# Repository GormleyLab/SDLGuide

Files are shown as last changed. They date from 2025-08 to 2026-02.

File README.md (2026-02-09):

<p align="center">
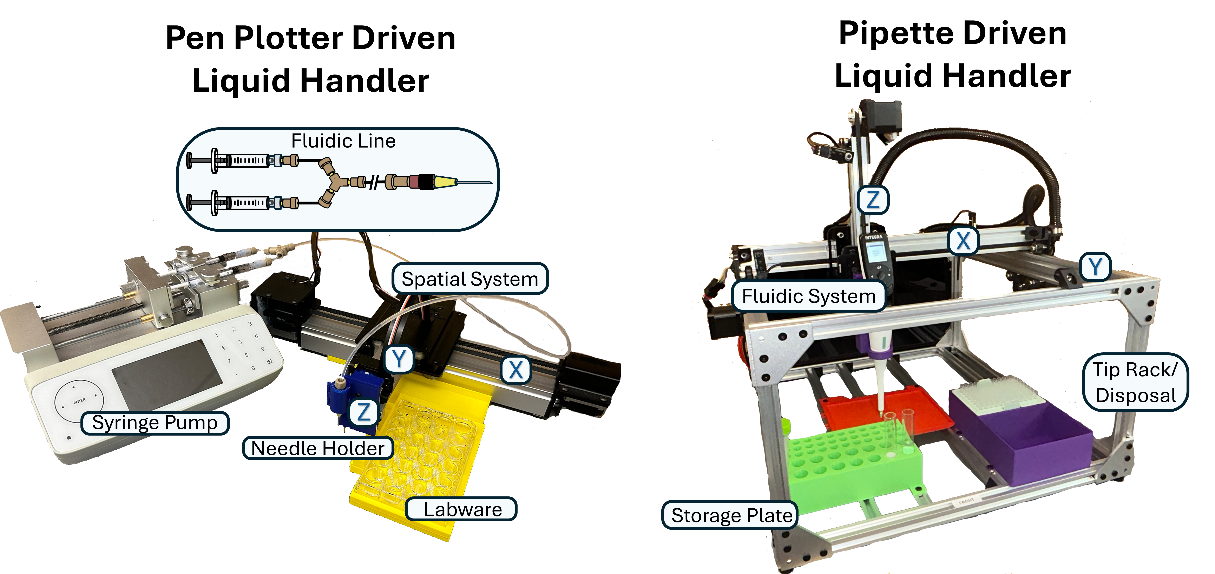
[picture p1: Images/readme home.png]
readme home
  
</p>

# Overview
Self-driving laboratories (SDLs) address a common bottleneck in experimentation: time and effort required to explore large parameter spaces. By combining automated experimentation with machine learning (ML) and Bayesian optimization (BO), an SDL can iteratively design experiments and learn from resulting data in a closed-loop, fully autonomous workflow.

This repository contains the instructions/code/files for the assembly and operations of a [Pen Plotter Driven Liquid Handler](/Pen%20Plotter%20Liquid%20Handler) and 
[Pipette Driven Liquid Handler](https://github.com/GormleyLab/Pipette-Liquid-Handler) as well as a collection of hands-on tutorial notebooks for active learning. Both devices are designed as low-cost automation tools to produce SDLs. The pen plotter-driven liquid handler is created using rigid pre-built spatial components that are modified to fit a user-developed 
fluidic system. The pipette-driven liquid handler is designed using modular components to provide the most flexibility, paired with a wireless autopipette.

In addition to hardware documentation, this repository includes a representative dataset generated using the SDL pipeline implemented here. The dataset was produced fully autonomously, and is used as an example to demonstrate how the design-build-test-learn (DBTL) workflow operates in practice, from experimental design through surrogate model training.
We use the optimization of a glucose oxidase (GOx) enzyme assay, which are common in wet-lab environments and are well suited as a representative example. 

---

## Repository Structure

Use this diagram to navigate the repository:

```
├── Hands-on Tutorial/           # AL and SDL tutorial notebooks and example data
│   ├── Notebook 1 - AL Tutorial.ipynb    # Principles of Active Learning
│   ├── Notebook 2 - SDL Tutorial.ipynb   # Real-world SDL application (enzyme assay)
│   ├── GOx Assay data_bank_renamed.csv  # Example GOx assay data for tutorials
│   ├── Older Iterations/               # Previous notebook versions
│   ├── requirements.txt                # Python dependencies for tutorials
│   └── README.md
│
├── Pen Plotter Liquid Handler/   # AxiDraw-based liquid handler (hardware + software)
│   ├── Pen Plotter SDL Software/ # GUI and automation software
│   │   ├── data/
│   │   │   └── GOx Assay data_bank.csv  # Validation dataset example
│   │   ├── src/
│   │   │   ├── sdlgui.py         # Main GUI layout and logic
│   │   │   ├── guifunctions.py   # Experiment setup, seed library, dispensing
│   │   │   ├── liquidhandler.py  # AxiDraw and syringe pump control
│   │   │   ├── dataprocessing.py # Data extraction, ML/AL integration
│   │   │   └── sdlvariables.py   # Global variables and experiment state
│   │   ├── resources/            # Icons and assets
│   │   ├── main.py               # Entry point (runs the GUI)
│   │   ├── requirements.txt
│   │   └── README.md
│   ├── SDL CAD Files/                  # 3D printable parts (STL, STEP)
│   ├── Pen Plotter LH Build Guide.pdf  # Building instructions for hardware
│   ├── SDL_SOP.pdf                     # Standard operating procedure
│   └── README.md
│
├── Pipette Liquid Handler/       # Wireless autopipette-based liquid handler (External Repo)
│   ├── Pipette SDL Software/    # GUI and automation software
│   │   ├── data/
│   │   │   └── GOx Assay data_bank.csv  # Validation dataset example
│   │   ├── src/
│   │   │   ├── sdlgui.py         # Main GUI layout and logic
│   │   │   ├── guifunctions.py   # Experiment setup, seed library, dispensing
│   │   │   ├── liquidhandler.py  # Pipette and pump control
│   │   │   ├── dataprocessing.py # Data extraction, ML/AL integration
│   │   │   └── sdlvariables.py   # Global variables and experiment state
│   │   ├── resources/            # Icons, tip positions, RemoteControl
│   │   ├── main.py               # Entry point (runs the GUI)
│   │   ├── requirements.txt
│   │   └── README.md
│   ├── Config Files/            # G-code and controller config (config.g, homeall.g, etc.)
│   ├── Pipette CAD Files/       # 3D design files (needle holder, vial rack, etc.)
│   ├── WIP Controller Program/   # Work-in-progress controller script alternatives
│   ├── Pipette Liquid Handler Building Guide.pdf
│   ├── Pipette Liquid Handler Parts List.xlsx
│   └── README.md
│
├── Images/                      # Figures for README and docs
├── index.html                    # Project homepage
├── LICENSE
└── README.md                     # This file
```

**Quick links:** [Tutorial Notebook 1 (AL)](/Hands-on%20Tutorial/Notebook%201%20-%20AL%20Tutorial.ipynb) · [Tutorial Notebook 2 (SDL)](/Hands-on%20Tutorial/Notebook%202%20-%20SDL%20Tutorial.ipynb) · [Pen Plotter Liquid Handler](/Pen%20Plotter%20Liquid%20Handler) · [Pipette Liquid Handler](https://github.com/GormleyLab/Pipette-Liquid-Handler)

---

## Tutorial Overview
The goal of the provided tutorial is to walk through the essentials of AL from start to finish, providing both conceptual explanations and hands-on code examples. A basic understanding of ML is assumed. If you're new to ML, we highly recommend reviewing [Part 1 of our User’s Guide series](https://doi.org/10.1021/acspolymersau.2c00037).
This guide is structured into three main tutorial notebooks, each building on the last for a smooth learning experience. Major points of interest from the guide provided are discussed below. 
### [Tutorial Notebook 1: Principles of Active Learning ](/Hands-on%20Tutorial/Notebook%201%20-%20AL%20Tutorial.ipynb)  
We begin with a simple, two-dimensional example of **Bayesian Optimization (BO)** applied to a black-box function. This notebook introduces the foundational concepts of active learning, inccluding data seeding, fitting surrogate models to data, and applying various acquisition functions to choose new sampling points.

### [Tutorial Notebook 2: Application to Real-World Data - Self-Driving Labs](/Hands-on%20Tutorial/Notebook%202%20-%20SDL%20Tutorial.ipynb)
Finally, we apply AL to a real experimental dataset involving enzymes. This notebook demonstrates how active learning can be used to efficiently select informative experiments and accelerate discovery in scientific research. This notebook explores: seed library generation (initial sampling) and closing the loop in the context of an SDL.

---

## Abstract
Experimentation is inherently difficult because most methods require substantial refinement, calibration, and validation before high-quality, reliable data can be collected. In most cases, experimental domains have multiple variables (i.e., high dimensionality), thus requiring their simultaneous optimization for single and multi-objective targets. Traditional experimental approaches rely on trial-and-error methods guided by rational decision making, but these become increasingly inefficient and ineffective as complex interactions between inputs limit our ability to capture underlying trends using conventional statistical approaches. Active learning and machine learning (AL/ML) combined with automation represents an indispensable approach for future laboratory productivity. However, a steep initial learning curve and high costs of instrumentation pose substantial barriers to adopt this powerful approach. To democratize access, we provide a comprehensive tutorial covering both the computational skills and hardware implementation necessary for self-driven experimental workflows. The accompanying open-source, low-cost liquid handling platforms offer practical templates for researchers adopting self-driving lab (SDL) methodologies.

---

## Authors:
Apostolos Maroulis, Dylan Waynor<br>
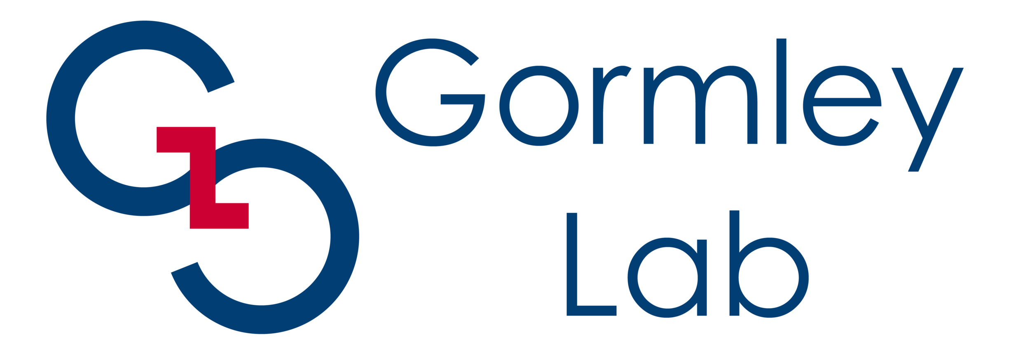
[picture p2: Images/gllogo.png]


Last Updated 01/29/2026
Version 1.0.0

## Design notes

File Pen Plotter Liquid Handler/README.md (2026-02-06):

# Self-Driving Lab based on AxiDraw and Syringe Pump
<p align="center">
axidraw
</p>

This project provides a graphical user interface (GUI) for automating enzyme assay experiments using a custom-built AxiDraw pen plotter liquid handler and a SpectraMax M2plate reader. It enables users to design, dispense, and analyze experimental formulations with minimal manual intervention.

## Features

- GUI for experiment setup and control
- Automated liquid handling via AxiDraw
- Integration with SpectraMax plate reader
- Seed library generation using Latin Hypercube Sampling
- Automated data collection and analysis
- Machine learning-driven experiment optimization (Gaussian Process, Expected Improvement)
- Custom CSV import/export for formulations and results

## Directory Structure

```
├── data/
│   └── GOx Assay data_bank.csv  # Validation dataset example
├── src/
│   ├── sdlgui.py         # Main GUI layout and logic
│   ├── guifunctions.py   # Experiment setup, seed library, dispensing
│   ├── liquidhandler.py  # AxiDraw and syringe pump control
│   ├── dataprocessing.py # Data extraction, ML/AL integration
│   └── sdlvariables.py   # Global variables and experiment state
├── resources/            # Icons and assets
├── main.py               # Entry point (runs the GUI)
├── requirements.txt
└── README.md
```

## Getting Started

### Prerequisites

- Python 3.8+
- [requirements.txt](requirements.txt) dependencies
- AxiDraw hardware and drivers
- SpectraMax plate reader and SDK
- ChemyX Syringe Pump SDK

### Installation

```sh
git clone <https://github.com/GormleyLab/SDLGuide>
cd Pen Plotter Liquid Handler/Pen Plotter SDL Software
pip install -r requirements.txt
```

### Running the Program

```sh
python main.py
```

## Usage

- **Home Tab:** Input reagent names, concentrations, pH, and group assignments. Import custom CSVs if needed.
- **Enzyme Assay Tab:** Configure experiment parameters, bounds, and desired activity. Start automated DBTL (Design-Build-Test-Learn) cycles.
- **Liquid Handler Tab:** Manually control AxiDraw for dispensing. (WIP)
- **Manual Tab:** Directly move AxiDraw and adjust pen/syringe settings.

---

### [Standard Operating Procedure (SOP)](SDL_SOP.pdf)

#### Self-Driven Lab: Custom Liquid Handler SOP

This SOP provides relevant information necessary for the overall viability and use of our device. It is reliant on basic understanding of other supplemental information: References to device setup will be attributed to the system build guide. References to ML/AL will be attributed to the tutorial notebooks. Some constraints of the device are in place to balance price effectiveness and system performance to provide a low-cost example of a liquid handler. The following is a quick start guide. It is highly recommended to follow the linked SOP above for an in-depth guide.

---

#### 1. Hardware Setup

To adapt the AxiDraw Pen Plotting machine for liquid handling, several modifications are required.  
Refer to the [Pen Plotter LH Build Guide](/Pen%20Plotter%20Liquid%20Handler/Pen%20Plotter%20LH%20Build%20Guide.pdf) for a detailed walkthrough of the necessary mechanical and hardware changes.  

1. **3D print the following custom parts**:  
   - AxiDraw Needle Holder  
   - AxiDraw Well Plate Platform  
   - Large Reservoir Insert  
2. **Modify** the AxiDraw hardware as outlined in the guide.  
3. **Assemble the fluidic loop** and connect it to both the Chemyx syringe pump and the AxiDraw.  
---

#### 2. Software Setup

- **AxiDraw:**  
  [AxiDraw Python API](https://axidraw.com/doc/py_api/#introduction)  
  If you haven't already, install:  
  `python -m pip install https://cdn.evilmadscientist.com/dl/ad/public/AxiDraw_API.zip`
- **Chemyx Syringe Pump:**  
  [Chemyx Python Setup Guide](https://chemyx.com/resources/knowledge-base/general-syringe-pump-info/computer-control-programs/python-program-installation-set-up-for-chemyx-fusion-200x-syringe-pump/)

---

#### 3. Preparation For Experimentation

**3.1 Calibration Protocol:**  
- Syringe Pump Calibration: Dispense triplicate known volumes, measure mass, and calibrate for loss.
- X/Y calibration: Use Manual UI to ensure coordinates for wells, waste, and reagents are accurate.
---

**3.2 Initial Setup**

- Fill the loop with water, minimizing air bubbles.
- Align the device with the Spectramax M2 by first raising the device to the appropriate height, and then ensuring the drawer opening just clears the cutout in the AxiDraw platform.
- Fill reservoirs 1 and 3 with DI water, leaving reservoir 2 (the middle) empty for waste.

---

**3.3 Experimental Setup**

- **Experiment Configuration:**
    - Prepare reagent list with concentrations and pHs.
    - Set mixing order and concentration bounds.
    - Define desired activity (ΔOD).
    - Ensure total dispensing volume per reagent is under 1.6ml.
    - Group reagents as needed; buffers can have different types and pHs.

---

**4.3 Notes on Experimentation**

- **Reagent Order:**  
  Dispense substrate last to control reaction start.
- **Locations:**  
  Log positions for reagents, waste, storage, and cleaning troughs in the script, as well as the pen down position to be at or near the bottom of each well without putting pressure.
- **Compatibility:**  
  Check tubing and luer compatibility for solvents and biologics. Adjust calibration for viscous materials.
- **Cleaning Protocol:**  
  Flush system after use, replace disposable components, and reprime as needed.

---

Thank you for trying to use our device as a platform for a SDL.

---

## Main Modules

- [`src/sdlgui.py`](src/sdlgui.py): Main GUI logic and layout
- [`src/guifunctions.py`](src/guifunctions.py): Experiment setup, seed library generation, dispensing instructions
- [`src/liquidhandler.py`](src/liquidhandler.py): AxiDraw and ChemyX pump control
- [`src/dataprocessing.py`](src/dataprocessing.py): Data extraction, analysis, machine learning
- [`src/sdlvariables.py`](src/sdlvariables.py): Global variables and experiment state

## License

MIT License

## Authors:
Apostolos Maroulis, Dylan Waynor<br>


Last Updated 01/29/2026
Version 1.0.0

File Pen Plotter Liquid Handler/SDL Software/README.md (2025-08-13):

# Self-Driving Lab based on AxiDraw and Syringe Pump
<p align="center">
axidraw
</p>

This project provides a graphical user interface (GUI) for automating enzyme assay experiments using a custom-built AxiDraw pen plotter liquid handler and a SpectraMax M2plate reader. It enables users to design, dispense, and analyze experimental formulations with minimal manual intervention.

## Features

- GUI for experiment setup and control
- Automated liquid handling via AxiDraw
- Integration with SpectraMax plate reader
- Seed library generation using Latin Hypercube Sampling
- Automated data collection and analysis
- Machine learning-driven experiment optimization (Gaussian Process, Expected Improvement)
- Custom CSV import/export for formulations and results

## Directory Structure

```
main.py
README.md
requirements.txt
data/
    GOx Assay data_bank.csv
resources/
    gl_logo.ico
src/
    dataprocessing.py
    guifunctions.py
    liquidhandler.py
    sdlgui.py
    sdlvariables.py
```

## Getting Started

### Prerequisites

- Python 3.8+
- [requirements.txt](requirements.txt) dependencies
- AxiDraw hardware and drivers
- SpectraMax plate reader and SDK
- ChemyX Syringe Pump SDK

### Installation

```sh
git clone <repo-url>
cd SDL_6_3_25
pip install -r requirements.txt
```

### Running the Program

```sh
python main.py
```

## Usage

- **Home Tab:** Input reagent names, concentrations, pH, and group assignments. Import custom CSVs if needed.
- **Enzyme Assay Tab:** Configure experiment parameters, bounds, and desired activity. Start automated DBTL (Design-Build-Test-Learn) cycles.
- **Liquid Handler Tab:** Manually control AxiDraw for dispensing. (WIP)
- **Manual Tab:** Directly move AxiDraw and adjust pen/syringe settings.

---

### [Standard Operating Procedure (SOP)](SDL_SOP.pdf)

#### Self-Driven Lab: Custom Liquid Handler SOP

This SOP provides relevant information necessary for the overall viability and use of our device. It is reliant on basic understanding of other supplemental information: References to device setup will be attributed to the system build guide. References to ML/AL will be attributed to the tutorial notebooks. Some constraints of the device are in place to balance price effectiveness and system performance to provide a low-cost example of a liquid handler. The following is a quick start guide. It is highly recommended to follow the linked SOP above for an in-depth guide.

---

#### 1. Hardware Setup

To adapt the AxiDraw Pen Plotting machine for liquid handling, several modifications are required.  
Refer to the [Pen Plotter LH Build Guide](https://github.com/Pasta1107/Users-Guide-to-SDL/blob/main/Pen%20Plotter%20Liquid%20Handler/Pen%20Plotter%20LH%20Build%20Guide.pdf) for a detailed walkthrough of the necessary mechanical and hardware changes.  

1. **3D print the following custom parts**:  
   - AxiDraw Needle Holder  
   - AxiDraw Well Plate Platform  
   - Large Reservoir Insert  
2. **Modify** the AxiDraw hardware as outlined in the guide.  
3. **Assemble the fluidic loop** and connect it to both the Chemyx syringe pump and the AxiDraw.  
---

#### 2. Software Setup

- **AxiDraw:**  
  [AxiDraw Python API](https://axidraw.com/doc/py_api/#introduction)  
  If you haven't already, install:  
  `python -m pip install https://cdn.evilmadscientist.com/dl/ad/public/AxiDraw_API.zip`
- **Chemyx Syringe Pump:**  
  [Chemyx Python Setup Guide](https://chemyx.com/resources/knowledge-base/general-syringe-pump-info/computer-control-programs/python-program-installation-set-up-for-chemyx-fusion-200x-syringe-pump/)

---

#### 3. Preparation For Experimentation

**3.1 Calibration Protocol:**  
- Syringe Pump Calibration: Dispense triplicate known volumes, measure mass, and calibrate for loss.
- X/Y calibration: Use Manual UI to ensure coordinates for wells, waste, and reagents are accurate.
---

**3.2 Initial Setup**

- Fill the loop with water, minimizing air bubbles.
- Align the device with the Spectramax M2 by first raising the device to the appropriate height, and then ensuring the drawer opening just clears the cutout in the AxiDraw platform.
- Fill reservoirs 1 and 3 with DI water, leaving reservoir 2 (the middle) empty for waste.

---

**3.3 Experimental Setup**

- **Experiment Configuration:**
    - Prepare reagent list with concentrations and pHs.
    - Set mixing order and concentration bounds.
    - Define desired activity (ΔOD).
    - Ensure total dispensing volume per reagent is under 1.6ml.
    - Group reagents as needed; buffers can have different types and pHs.

---

**4.3 Notes on Experimentation**

- **Reagent Order:**  
  Dispense substrate last to control reaction start.
- **Locations:**  
  Log positions for reagents, waste, storage, and cleaning troughs in the script, as well as the pen down position to be at or near the bottom of each well without putting pressure.
- **Compatibility:**  
  Check tubing and luer compatibility for solvents and biologics. Adjust calibration for viscous materials.
- **Cleaning Protocol:**  
  Flush system after use, replace disposable components, and reprime as needed.

---

Thank you for trying to use our device as a platform for a SDL.

---

## Main Modules

- [`src/sdlgui.py`](src/sdlgui.py): Main GUI logic and layout
- [`src/guifunctions.py`](src/guifunctions.py): Experiment setup, seed library generation, dispensing instructions
- [`src/liquidhandler.py`](src/liquidhandler.py): AxiDraw and ChemyX pump control
- [`src/dataprocessing.py`](src/dataprocessing.py): Data extraction, analysis, machine learning
- [`src/sdlvariables.py`](src/sdlvariables.py): Global variables and experiment state

## License

MIT License

## Authors:
Apostolos Maroulis, Dylan Waynor<br>


Last Updated ***

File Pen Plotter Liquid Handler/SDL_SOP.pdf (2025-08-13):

# Self-Driven Lab: Custom Liquid Handler SOP

By: Apostolos Maroulis, Dylan Waynor

This SOP provides relevant information necessary for the overall viability and use of our device. However, it is reliant on basic understanding of other supplemental information: References to device setup will be attributed to the system build guide. References to ML/AL will be attributed to the Google Colab notebook. Some constraints of the device are in place to balance price ef ectiveness and system performance to provide a low cost example of a liquid handler.

# Section 1. Hardware Setup

If a user creates a custom liquid handler based on the provided guide we would like to provide a small explanation of our example setup connected to a UV spectrophotometer. One of the major limitations of the device is its clearance when interacting with other devices to remedy this we used pipette tip holding boxes to elevate the device to the proper height. Any solid/stable object will work.

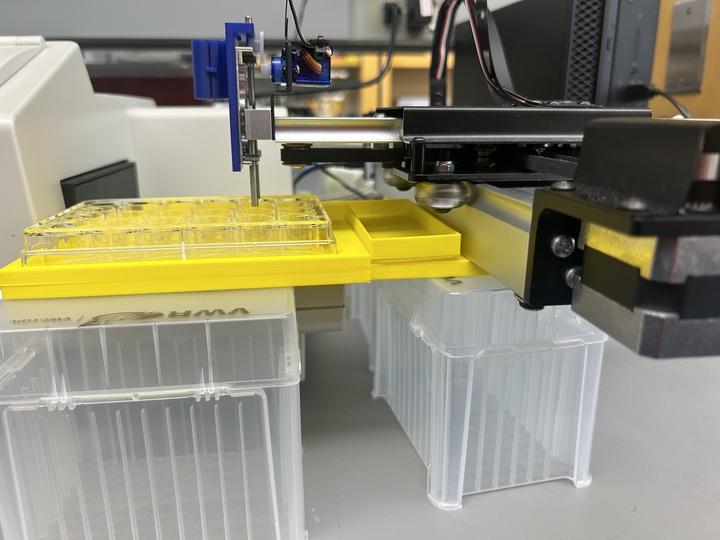
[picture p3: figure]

We align the device to the open tray of the UV spectrophotometer. The consistent measurement of this orientation is important as the positions of the measurement plate wells depend on your choice of positional values. (the positions attributed to the reagent wells and storage troughs should be always consistent as they are connected to the device).

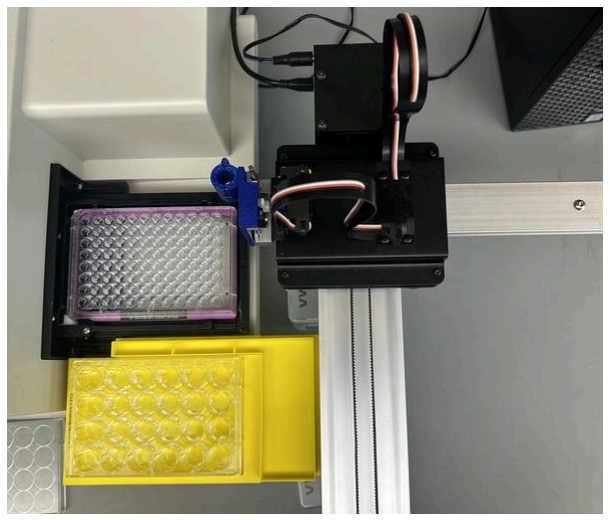
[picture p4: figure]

# Section 2. Software setup

To use the devices in the provided (or your own) python scripts it is important to download the relevant packages for the corresponding commands.
Axidraw - https://axidraw.com/doc/py_api/#introduction
One line install - python -m pip install https://cdn.evilmadscientist.com/dl/ad/public/AxiDraw_API.zip

Chemyx Syringe Pump -
https://chemyx.com/resources/knowledge-base/general-syringe-pump-info/computer-control-programs/python-program-installation-set-up-for-chemyx-fusion-200x-syringe-pump/ (https://chemyx.com/resources/knowledge-base/general-syringe-pump-info/computer-control-programs/python-program-installation-set-up-for-chemyx-fusion-200x-syri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)

# Section 3. Preparation For Experimentation

### 3.1. Calibration of Fluidic System

As you finish the construction of the fluidic system of the liquid handler there are additional setup steps before the device is truly experimentally ready.

### 3.1.1 Explanation of syringe choice and design

The complete design setup utilizes a two-syringe system that seeks to minimize variability of the syringe pump. Two 1ml syringes were chosen to leverage a smaller internal diameter to increase the reliability of dispense liquid at the flow rates used [Cite - Melanie A Jordan paper]. A longer syringe used within the system gives more available stroke length to leverage for better control of the stepper motor that controls the syringe pump. The discrete stopping positions of the syringe pump only allow for a specific volume of fluid to flow, and by having more discrete points it is possible to generate a greater number of specific volumes. The complete design setup utilizes a two-syringe system that seeks to minimize variability of the syringe pump. This is done by having longer syringes with small diameters. However, by optimizing for the most accuracy total volume does suffer. Larger syringes can be retrofitted into the design for an increase in possible sample volume for the cost of dispensing accuracy.

### 3.1.2 Storage Loop Setup

The fluidic system is based on a pressure driven syringe pump. To have the ability to draw and dispense small volumes using this system, we use a storage loop. This loop is filled with an incompressible experimentally inert fluid such as water to create consistent pressure using Pascal's principle. For this principle to be as true as possible, the minimization of air (bubbles) that is introduced into the storage solution is very important. To achieve as little air introduced into the syringes and loop the initial filling process should be done carefully.
To initially fill the syringes we fill a large vessel with the storage fluid (water) and fully submerge and evacuate the air that is trapped within. Then using the luer connectors reattach the partially filled tubes, and evacuate any remaining air out of the tubes (this is generally done by flicking the side of the tubes to jostle the settled air bubbles.
To generally reduce the reintroduction of air bubbles in the system we were able to improve performance by the leveling of your storage loop tubing to reduce air lock formation and waterfall flow at local maximas in height.
Another possible introduction of air within your syringes itself is dependent on the syringe choice. Lower quality syringes may not have plunger tips with perfect seals when drawing or dispensing at high rates. Due to this phenomena sometimes occurring the reduction in overall flow rates may help to improve inaccuracies as a tradeoff to total experimental time.

### 3.1.3 Air Gap

To separate the storage loop fluid from your drawn reagents we utilize a small air gap. This idea is not perfectly ideal as it introduces pressure loss when interacting with a compressible gas. However, compared to alternative methods like using an immiscible fluid as the representative gap, issues of mixing are greatly lessened. When the’ drawing protocol’ is executed during experimentation this air gap is formed as the buffer and should keep as a single unit if general bubble prevention protocol is followed. If it is noticed that there is a particular breakup of the air gap it may be produced by alterations in the surface energy of the tubing. To reduce this general cleaning protocol may be necessary.

# Section 4 Experimental Protocol

### Section 4.1 Manual Tab

Provided with the experimental UI, we created a mechanism to independently control the spatial system for the purposes of manual setup (Due to the easy to use interface on the Chemyx syringe pump the manual UI does not have controls for the pump). The manual setup stage of the system is very important for preallocating global variables before any automation steps are tried.

### 4.1.1 Variable Setup

- speed_pendown, speed_penup

These values designate the added degree of speed of the needle tip moving up and down at a location (range 0-110)Values can be changed if one would like to optimize the total time of experimentation. (The notation of variables using ‘pen’ is based on the fact that the axidraw system usually uses its z axis to move a pen up and down for writing tasks)

- pen up/down position and limit

These values contain the desired "top" and "bottom" positions of the z axis (range 0-100). A top position at 100 signifies that we would like to have the initial position at maximum height. The bottom positions may be altered to dispense into a vessel without hitting its bottom (in our case the bottom of a single well). A known issue is droplet formation occurring and adhering at the needle tip. It may be relevant to obtain precise measurements of the dispensing/ drawing position to allow for the reduction of droplet formation interfering with the accuracy of the device. To find optimal positioning there will be some trial and error.

- Positional calibrations (X/Y positions)

Using the Manual UI you are able to alter the X/Y spatial position of the axidraw system. This capability is introduced to allow the user to identify the specific coordinates that correlate with their experimentation. This feature is used to locate the position of the first well, waste, reagent holders. However this gained knowledge must be transferred into the relevant points within the script.

### 1.3 Calibration Protocol

To conclude general setup we suggest using a calibration step to understand how well you have done with setting up the fluid system and identify the loss that is generated through interactions of fluid mechanics. Some additional loss factors that are intrinsic to the system such as interactions with the tubing itself can not be helped. Therefore, it is necessary to retroactively correct the volumes used for experimentation for the loss that is consistent in your system.
To do this we use the relationship between mass and volume with a fluid of known density. We execute a sweep of volumes across the probable dispensing range (5-200ul) (Manually controlled through the Chemyx UI). In between each volume dispensed we measure the change in mass using a zeroed scale. This is recorded in triplicates to obtain readings that compare the desired dispensing volume and the measured volume. Using this data we can identify any loss trends and calibrate the system to correct for the error. Finally using the new calibration factor we identify the new accuracy using the same method. Alternative methods that can be used to identify the accuracy at specific volumes may include slowly drawing the dispensed volumes using a pipette. However, this method may be slower and more susceptible to human error.

### Section 4.2 Experimental tab

### 4.2.1 How to configure an experiment

You will need to design your parameter space, so you will need:
1. Reagent list with concentrations (and pHs if necessary)
2. Mixing Order
3. Reagent Concentration bounds (Final concentration in the well)
4. Desired activity (vMax)

5. The initial number of samples (Calculate the total volume of dispensing for each reagent and have it be under 1.6ml, including “filler”)
Capabilities of the program:
Can group reagents together, where each group gets a specific molarity based on the bounds of the reagents in the group. Then one of the reagents in the group will be selected. You can control what percentage of the seed library will contain reagents from a group. # Half of the seed library will contain reagents from a group.

Furthermore, you can add buffers, with different pHs. You can also have different buffer types, and then the program will select a buffer molarity, buffer type, and then a pH for each composition.

### 4.2.2 User Interface (UI) Info Guide

Once a wanted experimental pipeline has been thought up, one must use the UI to translate it into an automated loop.
1) You should first name the reagents in order of which they show up in your reagent reservoirs. The filler is not included in this bar, it is implied that the first reservoir is your filler material.
2) You must then identify if any reagent identifies. [i.e if you are using 3 different pH of the same buffer solution they would be in the same buffer 1 group]
3) Then you must input all reagent concentrations, each reagent concentration is non dimensionalized with respect to volume. [i.e. ABTS 200 is a 1X solution of 0.00173 mg/uL, while ABTS 100 represents a 0.5X solution] The order of concentration values determine the placement of your reagent reservoirs.
4) If a pH value is required [buffer group] you mark this reagent and leave all other reagents blank.

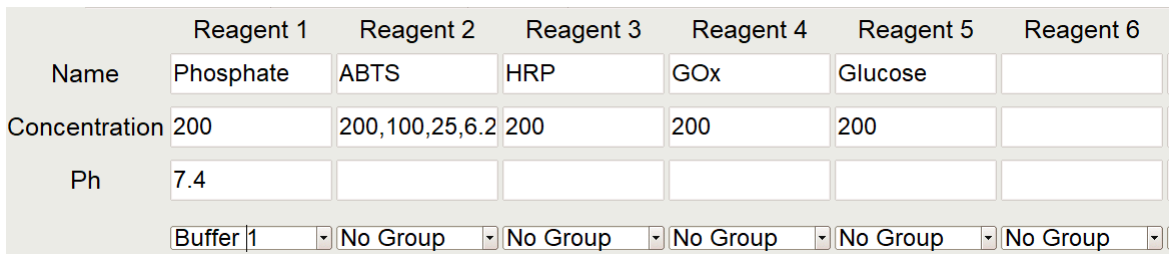
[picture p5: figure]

Non dimensionalized to volume : equivalent to the concentration value.

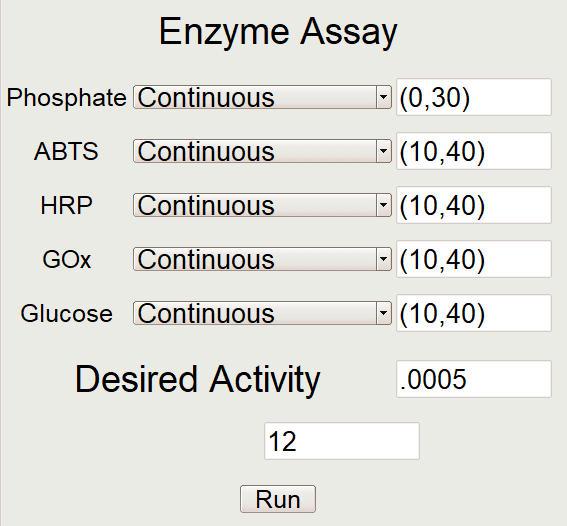
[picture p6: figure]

### 4.3. Notes on Experimentation

This section will identify helpful information for the development of your experimental procedures.

### 4.3.1 Choosing Reagent Order

A small note when setting up your design space and it is translated into the data sheet that runs the experiments. It is important to understand the ordering that the device will draw and dispense a specific reagent to formulate your mixtures. In our case, an enzymatic process does not begin its reaction until a specific substrate has been introduced. This required the ordering of the dispensed reagents to be tailored so that the reaction does not begin before we are ready to analyze the mixtures. The order may also need taking into account when thinking about possible mixing that could occur using the low cost system. Within the storage loop residue is reduced as much as it can with a cleaning stage, but the tubing may still have interactions with subsequent reagents. It may be necessary to order the reagents in order for reduction of fouling your experiment.

### 4.3.2 Reagent, Waste, Storage Solution, and Cleaning Troughs

For each component of your experiment the specific locations must be identified and logged into the script for use within the dispensing/drawing procedure. An issue that is apparent with the limited z axis depth is that to have additional objects within the range of the axidraw’s capabilities it must not interfere with X/Y movement. This produces a strict height requirement. To work within this constraint we utilized a 24-well well plate to hold our reagents, this is to hold a larger amount of volume of individual reagents that can be used uninterrupted over each iteration.. Our waste, storage, and cleaning troughs are all held in in-house creations of 3D printed troughs to be within these parameters. As an added complication to integrate with an analysis device it may be necessary to raise the entire device using stable structures to be able to correctly interface.

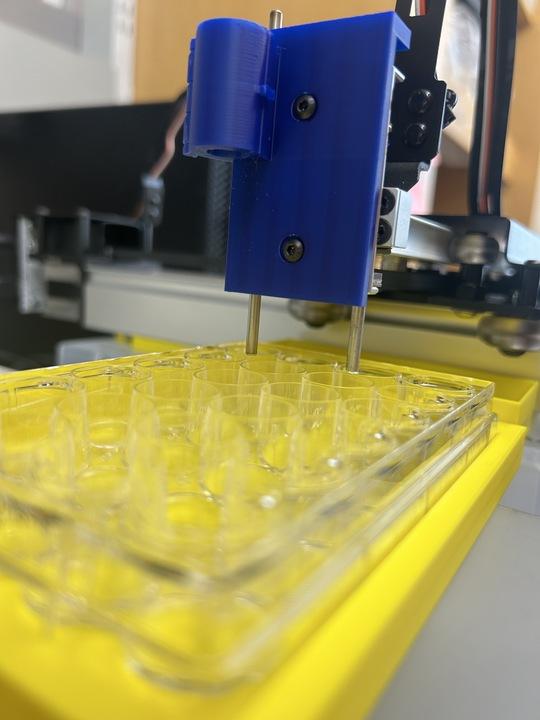
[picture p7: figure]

### 4.3.3 Compatibility (biologics, solvents, highly viscous materials)

Compatibility with solvents will be designated by tubing and luer products reference sheets. Compatibility with biological and viscous media may interfere with the fluid mechanics that drive our pressure driven system, however alterations in design or calibration may remedy these issues.

### 4.3.4 Cleaning Protocol

Standard care procedures should be taken into consideration. Flushing the system with a relevant cleaning solution after repeated use may be necessary. Replacement of disposable components (needle) may also be in order after repeated use. After cleaning protocol, it may be necessary to check the calibration.

Thank you for trying to use our device as a platform for a SDL. Please reach out if you have any further questions.

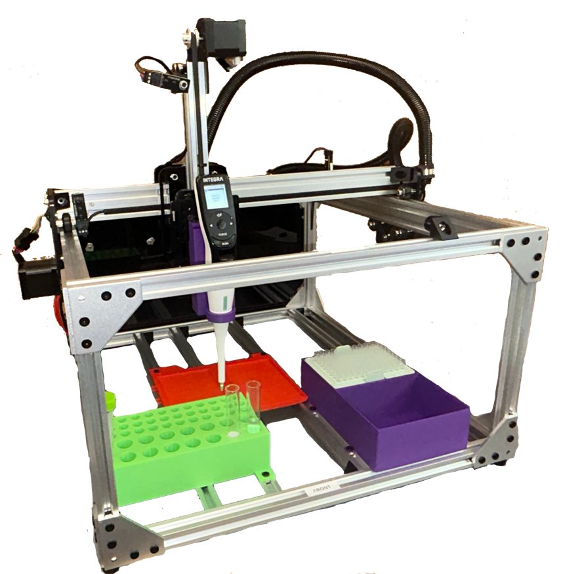
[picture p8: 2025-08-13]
Images/liquibot.png

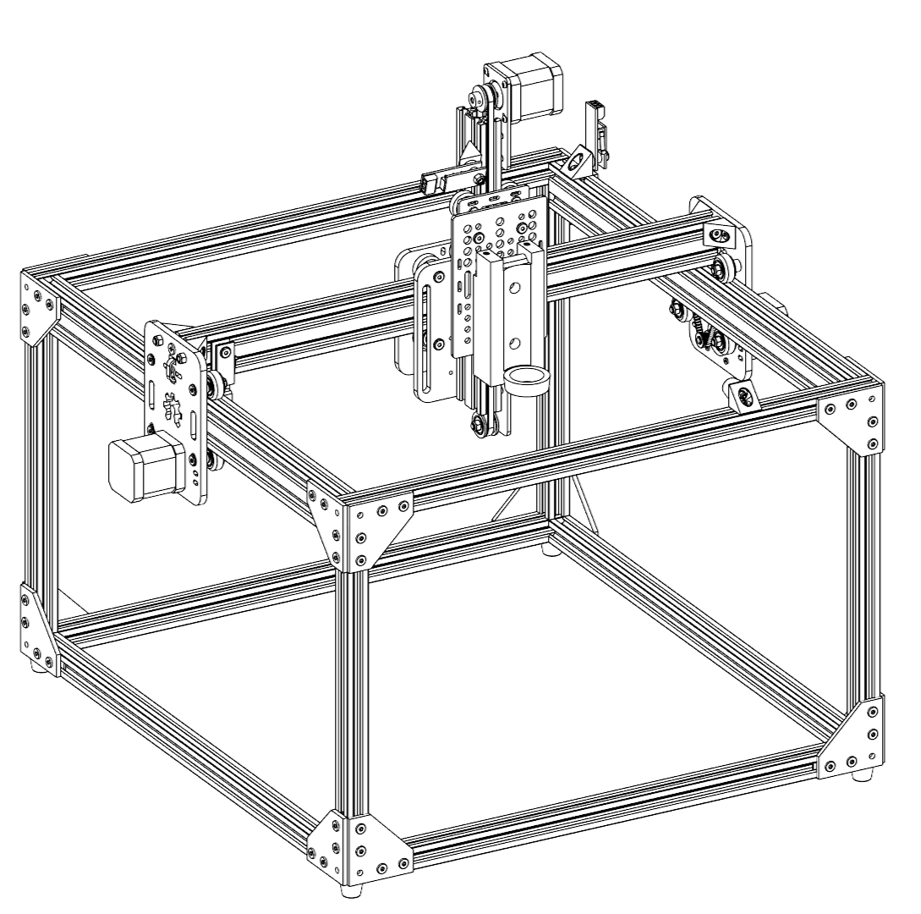
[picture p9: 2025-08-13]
Images/liquibot cad.png

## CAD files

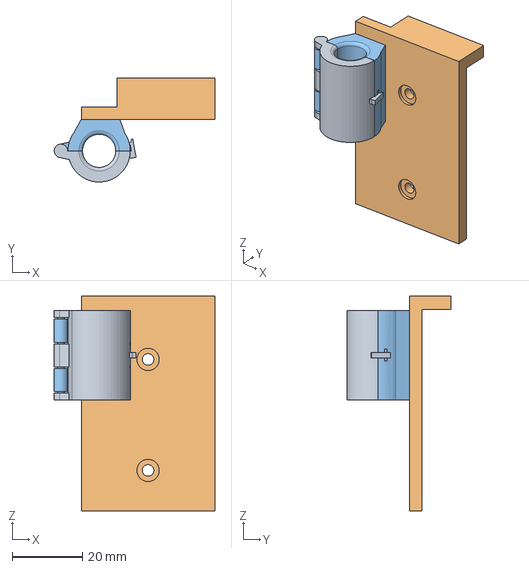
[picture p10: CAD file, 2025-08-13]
Pen Plotter Liquid Handler/SDL CAD Files/AxiDraw Needle Holder.step
45.8 x 29.7 x 61.4 mm

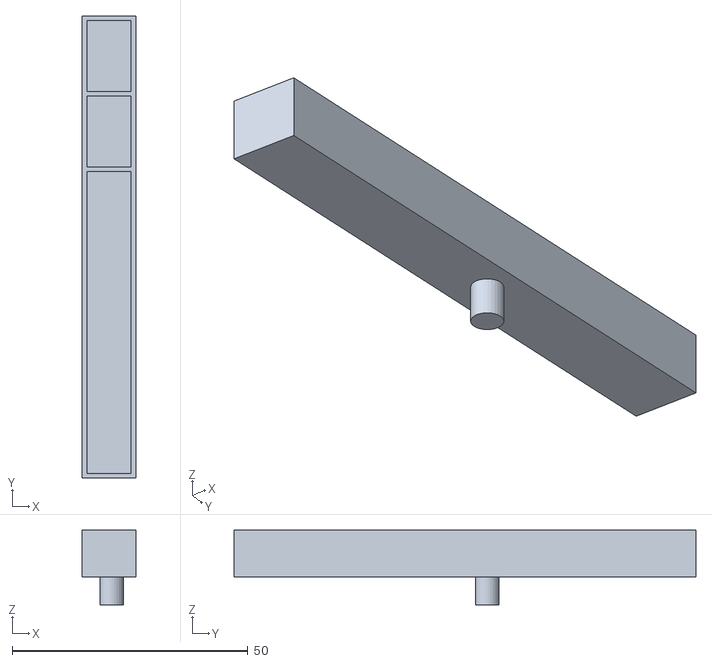
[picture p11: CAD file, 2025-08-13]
Pen Plotter Liquid Handler/SDL CAD Files/Small Reservoir Insert.stl
11.4 x 98.0 x 15.9

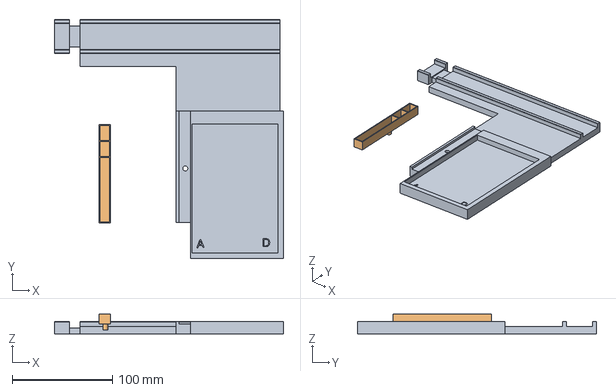
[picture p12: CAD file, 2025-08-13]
Pen Plotter Liquid Handler/SDL CAD Files/AxiDraw Well Plate Platform + Reservoir.step
227.9 x 237.7 x 19.6 mm

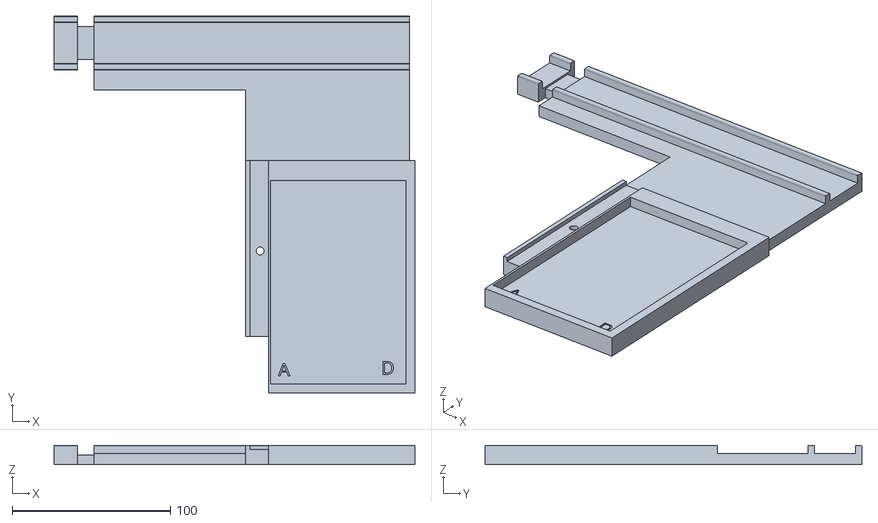
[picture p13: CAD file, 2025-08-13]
Pen Plotter Liquid Handler/SDL CAD Files/AxiDraw Well Plate Platform.stl
227.9 x 237.7 x 12.2

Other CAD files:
Pen Plotter Liquid Handler/SDL CAD Files/AxiDraw Needle Holder.stl

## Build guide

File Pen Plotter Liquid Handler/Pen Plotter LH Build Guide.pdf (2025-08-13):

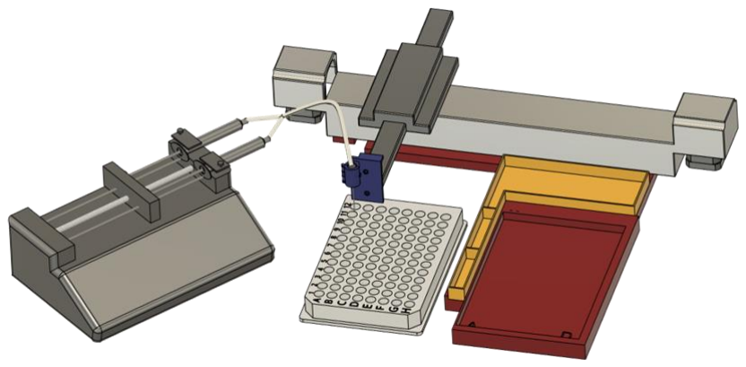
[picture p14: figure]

# Pen Plotter Liquid Handler Build Guide

By: Apostolos Maroulis, Dylan Waynor

## Parts List

AxiDraw Spacial System

Axidraw V3/B6 **get model number better specific specs**

3D Printed attachments (Files Included)

Fluidic Needle holder- PLA

Luer ‘straight line connector’ stabilizer - PLA

Stage/Platform - PLA

Fluidic System

40mm 20/22 gauge hypodermic needle

IDEX F-0.25-28/M-Luer (P-655)

IDEX Flngls Sys Short PEEK ⅛ 10pk (XP-335X)

38 in IDEX Tub FEP nat 1/8x.062 x 50ft (1521L)

(2X) IDEX F-Luer/F-Union (P-628)

(2X) BD 1ml syringe Luer-Lok tip

Plastic Tubing Cutter (A-327)

P-514 - PEEK Y Assembly 1/4-28 .060in thru hole

ChemyX Syringe pump Fusion 200x

*Some disposable parts of the system will need replacement between experiments due to contamination

## Spatial Movement: Axidraw System

The ‘out of the box’ Axidraw V3/B6 must be modified for our purposes. System differences in hardware may alter the appearance of some components of the guide, but the structure should be the same.

Step 1. Remove Pen Holder
1.1. Remove the two screws holding the outwards facing pen holder. This should expose the flat carriage. (hold onto the button head screws, they will be used in a later step)

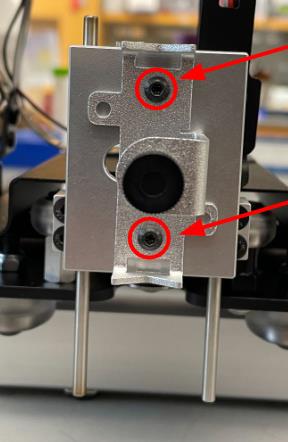
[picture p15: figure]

Step 2. Lowering the guide pins
2.1. (looking down from the top of the carriage) Remove the bottom four screws holding the carriage. Take into consideration which screw goes on each side. The screws are ‘side dependent’ and will produce resistance when reattached incorrectly.

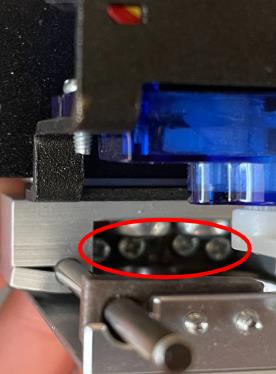
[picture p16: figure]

2.2. Once the screws are out, rotate the carriage piece outwards to clear the servo lever. If there is resistance, then slightly loosen the screws holding the top (brown) guide pieces (The guide pieces may fall, remember to keep track of side specific screws). To fully remove the carriage, tilt it up and slide it off from the top.

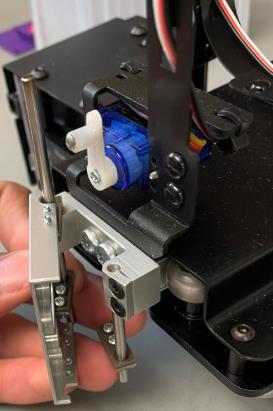
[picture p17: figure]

2.3. Loosen the four screws that clamp down on the guide pins. (Make sure to fully insert your allen key as to not strip the screws)

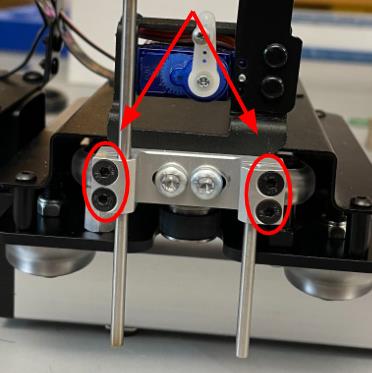
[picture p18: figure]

2.4. Adjust guide pin height
Set the top height of the longer bar to a length of 1.7in from the top of the guide pin clamp. (In the image below the carriage piece is on for reference height) To secure the guide pin’s height tighten the screws.
2.5. Re-install Carriage

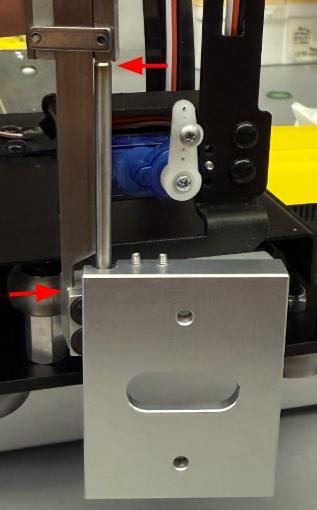
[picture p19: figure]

Insert the top of the carriage at an angle making sure that the top lip of the carriage goes BELOW the servo lever.

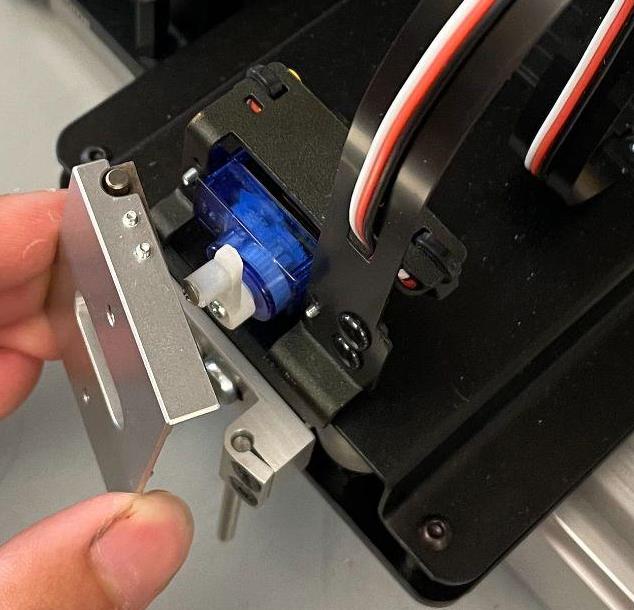
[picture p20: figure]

Re-attach the (brown) guide pins into the carriage by fastening the four screws. (To ensure smooth movement slight adjustments of the guide pins may be done by loosening and tightening)

2.6. Double check this last step by ensuring that the bottom end of the two pins do not protrude below the carriage and are properly stabilized.

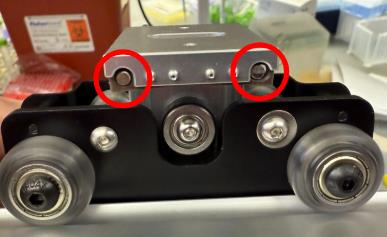
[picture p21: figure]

Step 3: Adjust the servo Lever position
The ‘out of the box’ servo lever position is adjusted by moving the placed screw. For our build we adjust the to the ‘fourth’ position (shown below).

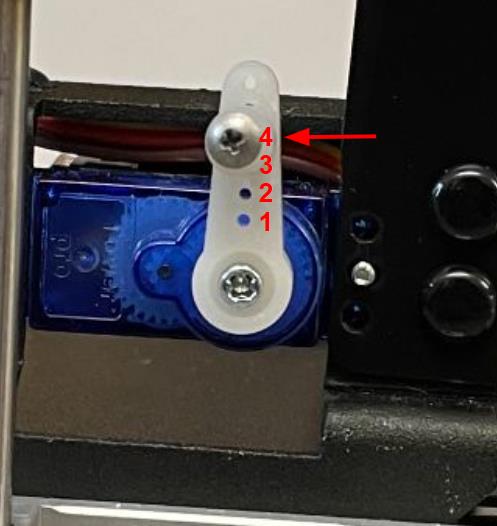
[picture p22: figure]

Step 4: Install 3D printed Needle holder

Lift the Carriage upwards below the servo lever. Place the printed needle holder above the servo lever. This should allow the servo lever to be sandwiched between the aluminum and printed lips.
Using The two screws taken off in Step 1, fasten the needle holder to the carriage.

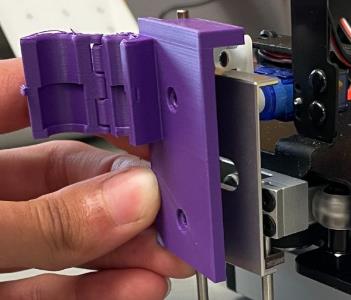
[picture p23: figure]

Step 5: Adjust the rubber feet of the AxiDraw
Carefully flip the device over. Unscrew the two button head screws, and move the rubber feet plate to 1.05 inches (26.67mm) from the black endplate. This introduces a standard base point of contact that will be used in the next step.
(for this step it may be beneficial to find two box-like objects to hold up the device at its motors)

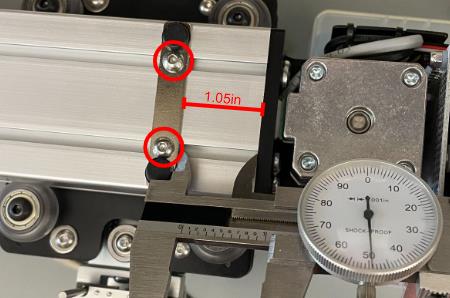
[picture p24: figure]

Step 6: Install 3D printed platform

Press the printed platform in so the notch lines up with the rubber feet plate, and ensure the two ridges fit in the slots on the underside of the device, as shown in the picture.

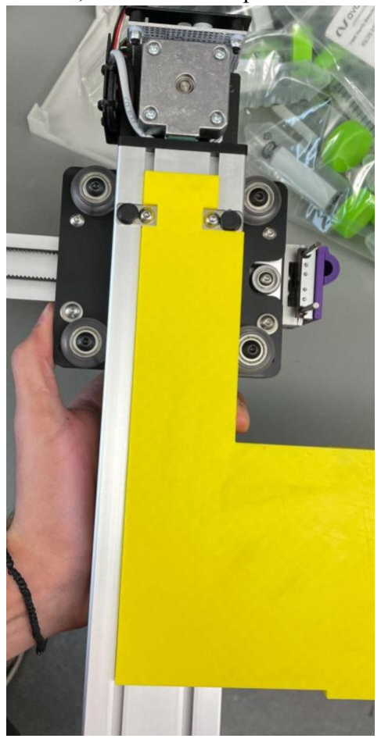
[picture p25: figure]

## Fluidic System construction

Step 1. Preparation of materials
1.1. Tubing Preparation
Cut the 1/8th OD tubing to 36 in (91.4 cm) long using a tubing cutter, or a utility knife, making sure to have a flat and perpendicular cut with no burrs
Also cut 2 short pieces of 1/8th OD tubing at 1 inch in length

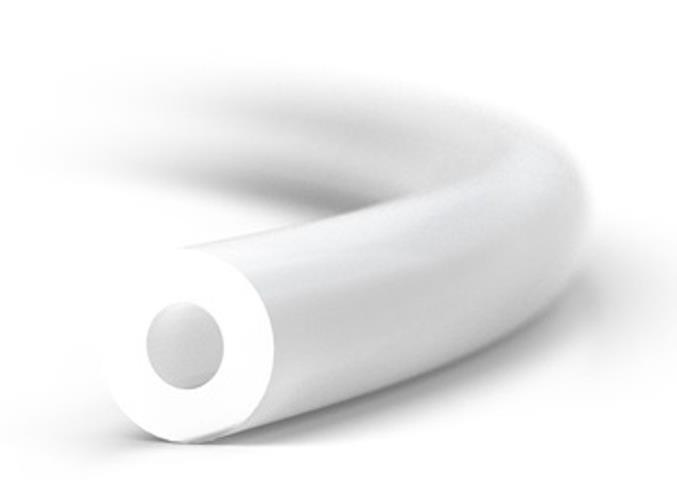
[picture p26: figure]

1.2. Needle Preparation
Snip the end of the hypodermic needle with a pair of side cutters, or other cutting tool. Make sure that you do not cave in the needle causing fluid transfer issues.

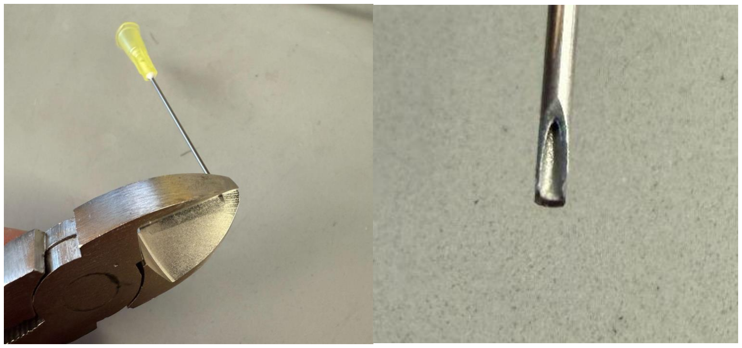
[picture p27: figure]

Step 2: Fluidic system assembly

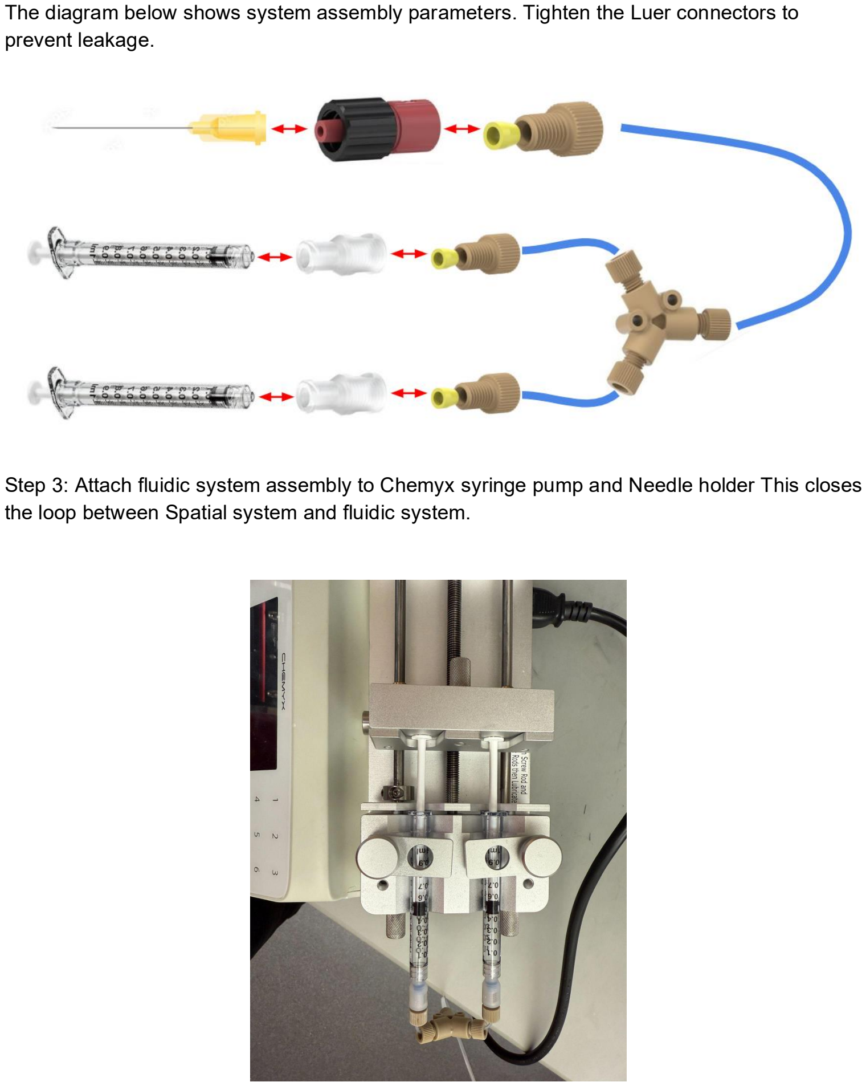
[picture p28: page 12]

The diagram below shows system assembly parameters. Tighten the Luer connectors to prevent leakage.

Step 3: Attach fluidic system assembly to Chemyx syringe pump and Needle holder This closes the loop between Spatial system and fluidic system.

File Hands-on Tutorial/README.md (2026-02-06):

> **Note**: The widgets in the user interface for notebook 2 do not render in the GitHub Preview. To view, you must download and run locally, or view the notebook in [Google Colab](https://colab.research.google.com/drive/1bBl2bTz1-Y4bTuPBKBZ19CbYj2Hosa-n?usp=sharing)
## Overview

The goal of this tutorial is to walk through the essentials of **Active Learning (AL)** from start to finish, providing both conceptual explanations and hands-on code examples. A basic understanding of **Machine Learning (ML)** is assumed. If you're new to ML, we highly recommend reviewing:

- **A User's Guide to Machine Learning**: https://doi.org/10.1021/acspolymersau.2c00037  
- **Accompanying ML Colab notebook**: https://www.gormleylab.com/MLcolab

### Tutorial Overview

This guide is structured into three main notebooks, each building on the last:

---

#### Tutorial Notebook 1: Principles of Active Learning  
We begin with a simple, two-dimensional example of **Bayesian Optimization (BO)** applied to a black-box function. This notebook introduces the foundational concepts of active learning, including:  
- Data seeding strategies
- Fitting a surrogate model (e.g., Gaussian process, random forest, neural network) to observed data  
- Using different acquisition functions to choose new sampling points

---

#### Tutorial Notebook 2: Application to Real-World Data - Self-Driving Labs

Here, we apply active learning to a **real experimental dataset** involving enzymes. This notebook demonstrates how active learning can be used to efficiently select informative experiments and accelerate discovery in scientific research. This notebook explores:

- Alternative data seeding strategies
- Structure of Self-Driving Labs
- Closing the Loop

---

## Authors:
Apostolos Maroulis, Dylan Waynor, Quinn Gallagher, Roshan Patel, Matthew Tamasi<br>


Last Updated 02/06/2026
Version 1.0.0

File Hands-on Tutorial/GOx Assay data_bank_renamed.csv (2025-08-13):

Well | Status | ABTS | HRP | GOx | Glucose | Slope | Iteration
A1 | TRUE | 16.25 | 43.75 | 18.75 | 23.75 | 0.000225111 | 1
B1 | TRUE | 48.75 | 28.75 | 31.25 | 26.25 | 0.000204 | 1
C1 | TRUE | 41.25 | 33.75 | 33.75 | 28.75 | 0.000269444 | 1
D1 | TRUE | 11.25 | 21.25 | 21.25 | 13.75 | 0.000116667 | 1
E1 | TRUE | 46.25 | 46.25 | 16.25 | 21.25 | 0.000191 | 1
F1 | TRUE | 31.25 | 41.25 | 38.75 | 33.75 | 0.000285889 | 1
G1 | TRUE | 13.75 | 13.75 | 28.75 | 46.25 | 0.000232222 | 1
H1 | TRUE | 18.75 | 18.75 | 46.25 | 18.75 | 0.000178667 | 1
A2 | TRUE | 36.25 | 16.25 | 48.75 | 43.75 | 0.000238444 | 1
B2 | TRUE | 43.75 | 38.75 | 41.25 | 31.25 | 0.000265667 | 1
C2 | TRUE | 33.75 | 48.75 | 36.25 | 38.75 | 0.000302 | 1
D2 | TRUE | 23.75 | 23.75 | 11.25 | 48.75 | 0.000230222 | 1
E2 | TRUE | 26.25 | 36.25 | 43.75 | 41.25 | 0.000389222 | 1
F2 | TRUE | 38.75 | 26.25 | 23.75 | 36.25 | 0.000216444 | 1
G2 | TRUE | 28.75 | 31.25 | 13.75 | 16.25 | 7.64E-05 | 1
H2 | TRUE | 21.25 | 11.25 | 26.25 | 11.25 | 8.43E-05 | 1
A3 | TRUE | 10 | 34.61538462 | 19.23076923 | 50 | 0.000390889 | 2
B3 | TRUE | 40.76923077 | 44.87179487 | 40.76923077 | 10 | 0.000348667 | 2
C3 | TRUE | 41.79487179 | 44.87179487 | 48.97435897 | 10 | 0.000343556 | 2
D3 | TRUE | 48.97435897 | 45.8974359 | 41.79487179 | 10 | 0.000193556 | 2
E3 | TRUE | 14.1025641 | 34.61538462 | 30.51282051 | 50 | 0.000420222 | 2
F3 | TRUE | 46.92307692 | 45.8974359 | 46.92307692 | 10 | 0.000175889 | 2
G3 | TRUE | 10 | 33.58974359 | 42.82051282 | 50 | 0.000602556 | 3
H3 | TRUE | 24.35897436 | 34.61538462 | 15.12820513 | 50 | 0.000333889 | 3
A4 | TRUE | 23.33333333 | 34.61538462 | 14.1025641 | 50 | 0.000308778 | 3
B4 | TRUE | 11.02564103 | 33.58974359 | 43.84615385 | 50 | 0.000604556 | 3
C4 | TRUE | 18.20512821 | 33.58974359 | 50 | 50 | 0.000532111 | 3
D4 | TRUE | 15.12820513 | 33.58974359 | 46.92307692 | 50 | 0.000490556 | 3
E4 | TRUE | 10 | 33.58974359 | 44.87179487 | 50 | 0.000635333 | 4
F4 | TRUE | 27.43589744 | 34.61538462 | 17.17948718 | 50 | 0.000346111 | 4
G4 | TRUE | 25.38461538 | 34.61538462 | 15.12820513 | 50 | 0.000351556 | 4
H4 | TRUE | 11.02564103 | 33.58974359 | 44.87179487 | 50 | 0.000534111 | 4
A5 | TRUE | 18.20512821 | 33.58974359 | 50 | 50 | 0.000488556 | 4
B5 | TRUE | 15.12820513 | 33.58974359 | 47.94871795 | 50 | 0.000494333 | 4
C5 | TRUE | 10 | 33.58974359 | 44.87179487 | 50 | 0.000668 | 5
D5 | TRUE | 27.43589744 | 34.61538462 | 17.17948718 | 50 | 0.000379556 | 5
E5 | TRUE | 25.38461538 | 34.61538462 | 15.12820513 | 50 | 0.000334222 | 5
F5 | TRUE | 11.02564103 | 33.58974359 | 44.87179487 | 50 | 0.000543667 | 5
G5 | TRUE | 18.20512821 | 33.58974359 | 50 | 50 | 0.000502778 | 5
H5 | TRUE | 15.12820513 | 33.58974359 | 47.94871795 | 50 | 0.000475333 | 5
A6 | FALSE | 10 | 33.58974359 | 44.87179487 | 50 | 0.000605444
B6 | FALSE | 27.43589744 | 34.61538462 | 16.15384615 | 50 | 0.000331444
C6 | FALSE | 25.38461538 | 34.61538462 | 14.1025641 | 50 | 0.000316889
D6 | FALSE | 11.02564103 | 33.58974359 | 44.87179487 | 50 | 0.000449556
E6 | FALSE | 18.20512821 | 33.58974359 | 50 | 50 | 0.000473333
F6 | FALSE | 15.12820513 | 33.58974359 | 47.94871795 | 50 | 0.000436111
G6 | FALSE | 10 | 33.58974359 | 44.87179487 | 50
H6 | FALSE | 27.43589744 | 34.61538462 | 17.17948718 | 50
A7 | FALSE | 25.38461538 | 34.61538462 | 15.12820513 | 50
B7 | FALSE | 11.02564103 | 33.58974359 | 45.8974359 | 50
C7 | FALSE | 18.20512821 | 33.58974359 | 50 | 50
D7 | FALSE | 15.12820513 | 33.58974359 | 47.94871795 | 50
E7 | FALSE
F7 | FALSE
G7 | FALSE
H7 | FALSE
A8 | FALSE
B8 | FALSE
C8 | FALSE
D8 | FALSE
E8 | FALSE
F8 | FALSE
G8 | FALSE
H8 | FALSE
A9 | FALSE
B9 | FALSE
C9 | FALSE
D9 | FALSE
E9 | FALSE
F9 | FALSE
G9 | FALSE
H9 | FALSE
A10 | FALSE
B10 | FALSE
C10 | FALSE
D10 | FALSE
E10 | FALSE
F10 | FALSE
G10 | FALSE
H10 | FALSE
A11 | FALSE
B11 | FALSE
C11 | FALSE
D11 | FALSE
E11 | FALSE
F11 | FALSE
G11 | FALSE
H11 | FALSE
A12 | FALSE
B12 | FALSE
C12 | FALSE
D12 | FALSE
E12 | FALSE
F12 | FALSE
G12 | FALSE
H12 | FALSE

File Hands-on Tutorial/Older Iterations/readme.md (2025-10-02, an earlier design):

# Older Iterations of Active Learning Hands-On Tutorial

These notebooks can be used to supplement some information and skills that can be used in developing your **Active Learning (AL)** campaign. They are a slower paced, more in depth guide on active learning, with the SDL tutorial remaining the same.

## Overview

The goal of this tutorial is to walk through the essentials of AL from start to finish, providing both conceptual explanations and hands-on code examples. A basic understanding of **Machine Learning (ML)** is assumed. If you're new to ML, we highly recommend reviewing:

- **A User's Guide to Machine Learning**: https://doi.org/10.1021/acspolymersau.2c00037  
- **Accompanying ML Colab notebook**: https://www.gormleylab.com/MLcolab

### Tutorial Overview

This guide is structured into three main notebooks, each building on the last:

---

#### [Tutorial Notebook 1: Bayesian Optimization in 1D](https://github.com/GormleyLab/SDLGuide/blob/main/Hands-on%20Tutorial/Notebook%201%20AL%20Tutorial.ipynb)  
We begin with a simple, one-dimensional example of **Bayesian Optimization (BO)** applied to a black-box function. This notebook introduces the foundational concepts of active learning, including:  
- Fitting a Gaussian Process (GP) to observed data  
- Using acquisition functions to choose new sampling points

---

#### [Tutorial Notebook 2: Deeper dive into Active Learning](https://github.com/GormleyLab/SDLGuide/blob/main/Hands-on%20Tutorial/Notebook%202%20AL%20Tutorial.ipynb)

Next, we extend the BO framework to higher-dimensional spaces. This notebook explores:

- Acquisition functions in complex domains
- The trade-off between exploitation (sampling where predictions are high) and exploration (sampling where uncertainty is high)
- Alternative ML models and their effects on BO
- Alternative BO algorithms and their effects on optimization efficiency

---

#### [Tutorial Notebook 3: Application to Real-World Data - Self-Driving Labs](https://github.com/GormleyLab/SDLGuide/blob/main/Hands-on%20Tutorial/Notebook%203%20AL%20Tutorial.ipynb)

Finally, we apply active learning to a **real experimental dataset** involving enzymes. This notebook demonstrates how active learning can be used to efficiently select informative experiments and accelerate discovery in scientific research. This notebook explores:

- Seed Library Generation (Initial sampling)
- Structure of Self-Driving Labs
- Closing the Loop

---

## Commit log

2025-08-13 new file: .gitmodules new file: AutoPipette Liquid Handler/AutoPipette CAD Files/Needle holder v7.f3d new file: AutoPipette Liquid Handler/AutoPipette CAD Files/Pipette holder clamp v11.f3d new file: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
    [AutoPipette Liquid Handler Parts List.xlsx, AxiDraw Needle Holder.step, AxiDraw Needle Holder.stl, AxiDraw Well Plate Platform + Reservoir.step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]
2025-08-19 deleted: AutoPipette Liquid Handler/AutoPipette CAD Files/Needle holder v7.f3d deleted: AutoPipette Liquid Handler/AutoPipette CAD Files/Pipette holder clamp v11.f3d deleted: AutoPipette Liquid Handl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
    [AutoPipette Liquid Handler Parts List.xlsx, Computed Positions.csv, GOx Assay data_bank.csv, Labware Positions Sheet.xlsx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]
2025-08-19 modified: .gitmodules new file: Pipette-Liquid-Handler
2025-08-19 renamed: Hands-on Tutorial/Section 1 AL Tutorial.ipynb -> Hands-on Tutorial/Notebook 1 AL Tutorial.ipynb renamed: Hands-on Tutorial/Section 2 AL Tutorial.ipynb -> Hands-on Tutorial/Notebook 2 AL Tuto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
    [GOx Assay data_bank.csv]
2025-08-20 modified: .gitmodules modified: Pipette-Liquid-Handler modified: index.html
2025-09-18 modified: Pipette-Liquid-Handler
2025-10-02 new file: Hands-on Tutorial/Notebook 1 - AL Tutorial.ipynb new file: Hands-on Tutorial/Notebook 2 - SDL Tutorial.ipynb renamed: Hands-on Tutorial/Notebook 1 AL Tutorial.ipynb -> Hands-on Tutorial/Old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
2025-10-02 modified: Pen Plotter Liquid Handler/README.md modified: Pipette-Liquid-Handler modified: README.md modified: index.html
2026-01-29 modified: Hands-on Tutorial/Notebook 2 - SDL Tutorial.ipynb
    [data_bank.csv]
2026-01-29 deleted: Hands-on Tutorial/NOTEBOOK_WIDGETS_GITHUB.md deleted: Hands-on Tutorial/all_combinations.csv deleted: Hands-on Tutorial/data_bank.csv deleted: Hands-on Tutorial/fix_widget_metadata_for_githu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
    [data_bank.csv]
2026-02-02 modified: Hands-on Tutorial/Notebook 1 - AL Tutorial.ipynb modified: Hands-on Tutorial/Notebook 2 - SDL Tutorial.ipynb modified: Pen Plotter Liquid Handler/README.md deleted: Pipette Liquid Handler m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
